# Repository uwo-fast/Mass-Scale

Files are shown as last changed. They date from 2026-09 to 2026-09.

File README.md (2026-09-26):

# Mass Scale

> A 3-D printed digital scale built around a strain-gauge load cell, an HX711
> amplifier and an Arduino Nano, read over serial for data logging. Three
> generations in one repository: Benjamin Hubbard's 2019 OS Nano Balance, the
> lab-grade scale Michigan Tech's MOST lab published in *Instruments* in 2020,
> and the FAST research group's 2025–26 revival, which is the current design.





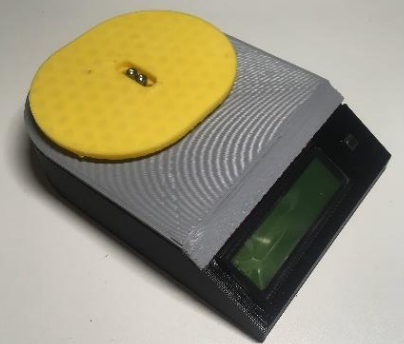
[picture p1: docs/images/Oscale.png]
The assembled 2020 scale: the printed housing with its yellow weighing platform and the LCD


## Overview

The scale is a printed housing that holds a single-point parallel-beam load
cell (a TAL220 for kilogram ranges or a TAL221 for gram ranges), an HX711
24-bit load-cell amplifier, an Arduino Nano, a push-button, and optionally a
16 × 2 LCD. Everything runs from 5 V over USB, so a phone charger or a
computer's USB port powers it. The button tares the scale; over serial, a
computer reads it continuously and calibrates it against a known mass.

**The current design** is the revival's:

- [`cad/openscad/`](cad/README.md#the-current-design) — the OpenSCAD v2
  enclosure, with a bevelled front face for the LCD, and the platter that
  fits over it. Parametric: the dimensions are variables at the top of
  `assembly.scad`. [`cad/openscad-v3/`](cad/README.md) is the next revision,
  in progress, with a sliding, latching lid.
- [`firmware/mass-scale/`](firmware/README.md) — the rewritten firmware:
  calibration over serial, stored in EEPROM; tare from the button or serial;
  a non-blocking readout of raw and calibrated values ten times a second;
  guards against a missing amplifier or a corrupt calibration.

The 2020 design and firmware are kept in full and still checked, and the 2019
files are kept for reference and attribution; see [History](#history) and
[`docs/sources.md`](docs/sources.md).

The scale is described in:

> Hubbard BR, Pearce JM (2020). *Open-Source Digitally Replicable Lab-Grade
> Scales.* Instruments 4(3): 18.
> [doi:10.3390/instruments4030018](https://doi.org/10.3390/instruments4030018)

The paper tests three load cells, a 5 kg TAL220 and 500 g and 100 g TAL221s,
against two commercial laboratory balances and against standard masses. It
reports repeatability within 0.05 g for all three, down to a standard deviation
of about 0.005 g for the 100 g cell, readings that track the laboratory balances
linearly, and a parts cost of about USD 51 without an LCD or USD 66 with one
(USD 41 and 47 counting only the parts used out of bulk packs), against USD 110
to 289 for commercial scales with a serial interface.

**Status.** The v2 enclosure and platter have been printed, and the firmware
builds and has had its calibration and readout reworked since; neither has
been characterised the way the paper characterised the 2020 scale. The v2 parts do not yet model the load cell's
mounting or the electronics' seats, and v3 is unfinished; the firmware does
not yet have the 2020 firmware's SMA protocol, OLED support or averaging
filter. See [Known problems](#known-problems) and the issues.

## Repository layout

- `cad/` — every generation of the printed parts: `openscad/` (current),
  `openscad-v3/` (in progress), `openscad-v1/`, `freecad-2020/` with the
  published STLs, `freecad-2019/`, `openscad-2019/`
  ([details](cad/README.md))
- `firmware/` — `mass-scale/` (current), `most-massbalance-2020/` (the paper's
  sketch and the library form of it), `os-nano-balance-2019/`
  ([details](firmware/README.md))
- `electronics/` — the 2020 Fritzing circuit and its breadboard and schematic
  views ([details](electronics/README.md)); the pins are the same in every
  generation
- `bom/` — the paper's bill of materials ([as tables](bom/README.md))
- `docs/` — the 2020 [operation guide](docs/operation.md), the
  [breadboard assembly guide](docs/electronics-assembly.md),
  [the paper](docs/paper/), the [datasheets](docs/datasheets/README.md), the
  [test data](docs/test-data/README.md), the
  [serial protocol notes](docs/serial-protocol/README.md), and
  [sources](docs/sources.md) for everything else
- `tools/` — the STL and FreeCAD comparison scripts the checks use

## Getting started

You need [OpenSCAD](https://openscad.org/),
[arduino-cli](https://arduino.github.io/arduino-cli/), Python 3, `curl`,
`unzip` and [just](https://github.com/casey/just). FreeCAD 0.18 or later
opens the 2020 and 2019 CAD; it is not needed for the checks.

```sh
just firmware-deps   # install the pinned AVR core and libraries; fetch the pinned HX711 and LiquidCrystal
just check           # check the FreeCAD files and STLs, render every OpenSCAD part, build every firmware target (what CI runs)
just render          # write every OpenSCAD part to build/cad/openscad/
just firmware        # build every firmware target and leave the .hex files under build/firmware/
```

`OPENSCAD` names the OpenSCAD command when it is not on `PATH`, and
`OPENSCAD_FLAGS` adds flags to every render.

To build one: render `enclosure` and `platter` from `cad/openscad/`
(`just render`, or the customizer in OpenSCAD's GUI with `assembly.scad`), buy
the parts in [`bom/`](bom/README.md) (the electronics are the same in every
generation), wire them as in [`firmware/README.md`](firmware/README.md#wiring)
or the [breadboard guide](docs/electronics-assembly.md), and flash the
firmware:

```sh
just firmware
arduino-cli upload --fqbn arduino:avr:nano -p /dev/ttyUSB0 --input-dir build/firmware/mass-scale
```

Then open a serial monitor at 115200 baud (newline line endings). The scale
tares itself at start-up and prints `Raw: …, Mass: … g`; `t` or the button
tares it, and `c`, `u00` with the platter empty, then `a<grams>` with a known
mass on it, calibrates it and stores the result in EEPROM. Any serial client
that logs, such as PuTTY, records the readings.
[`firmware/mass-scale/README.md`](firmware/mass-scale/README.md) has the
details; [`docs/operation.md`](docs/operation.md) describes the 2020 firmware
and its SCP-0499 commands.

## Known problems

Carried over from the published designs, or opened by the revival, and not
fixed here; each is an issue:

- **Drift after power-on.** The paper observes that the reading drifts
  noticeably when the scale is first switched on, largely with temperature,
  and recommends a warm-up; no firmware here compensates for temperature.
- **The current firmware lacks features of the 2020 firmware:** the SMA
  SCP-0499 serial protocol, the OLED display driver, the configurable
  averaging filter, and the library form that other sketches can use.
- **The v2 enclosure has no load-cell mount or electronics seats**, and v3 is
  unfinished; the 2020 FreeCAD design has both.
- **The OLED display is unstable on small boards** (2020 library). Upstream's
  README says an OLED needs more RAM than a Nano has (use a Nano Every or a
  Mega), and that turning an OLED off and straight back on with `XL` can stall
  the firmware.
- **The housing is light.** The paper notes that the printed housing would
  deform under heavy loads, which side-loads the load cell; higher-capacity
  cells want a stiffer housing.
- **The published 2020 `Base.stl` predates the FreeCAD document.** It is
  1.25 % smaller than the base the document builds, with the same outline; the
  other three STLs match the document (see [`cad/README.md`](cad/README.md)).
- **The paper's sketch was Windows-only as published**: its includes used
  backslashes, fixed here in three one-line commits (see
  [`CHANGELOG.md`](CHANGELOG.md)). The 2019 sketch is kept as published and
  is not built.
- **Third-party datasheets** are redistributed without a licence statement;
  see [`LICENSING.md`](LICENSING.md).

## History

The repository carries all three histories, joined without rewriting any of
them. An annotated tag marks each source as it was:

| Generation | What | Tags |
| --- | --- | --- |
| **2019 — OS Nano Balance**, Benjamin Hubbard | The first version: an Arduino Nano, an HX711 and a TAL220 or TAL221 in printed parts drawn first in OpenSCAD and then in FreeCAD, with a sketch that calibrates from a button against a fixed mass. Published at [brhubbar/OS_Nano_Balance](https://github.com/brhubbar/OS_Nano_Balance) and on Appropedia as [3D printed digital balance](https://www.appropedia.org/3D_printed_digital_balance). Here: `firmware/os-nano-balance-2019/`, `cad/freecad-2019/`, `cad/openscad-2019/` | `mtu-nanobalance-2019` |
| **2020 — the MOST lab-grade scale**, Benjamin Hubbard and Joshua Pearce | The scale the paper describes: one parametric FreeCAD document, the DigitalMassBalance 2.0.1 sketch implementing the SMA SCP-0499 serial protocol, and its later library form MOST_MassBalance 3.4.0. Published in [*Instruments*](https://doi.org/10.3390/instruments4030018), on [OSF me9a8](https://osf.io/me9a8), at [gitlab.com/mtu-most/most_massbalance](https://gitlab.com/mtu-most/most_massbalance) and on [Appropedia](https://www.appropedia.org/Open_Source_Digitally_Replicable_Lab-Grade_Scales). Here: `cad/freecad-2020/`, `firmware/most-massbalance-2020/`, `electronics/`, `bom/`, `docs/` | `mtu-instruments-2020` (the firmware as published with the paper), `mtu-final-2021` (upstream's last commit), `mtu-osf-2020` (the OSF files as published), and upstream's own `v3.0.0` to `v3.4.0` |
| **2025–26 — the FAST revival**, Cameron Brooks | A new OpenSCAD enclosure and platter (v2), a next revision in progress (v3) using the [load-cell-scad](https://github.com/CameronBrooks11/load-cell-scad) library, and a rewrite of the 2019 firmware with calibration over serial. Published at [uwo-fast/mass-scale](https://github.com/uwo-fast/mass-scale), which this repository continues. Here: `cad/openscad/`, `cad/openscad-v3/`, `cad/openscad-v1/`, `firmware/mass-scale/` | `fast-revival-2026` |

[`CHANGELOG.md`](CHANGELOG.md) lists what changed when the histories were
joined and when the 2020 files were imported; [`docs/sources.md`](docs/sources.md)
says where every file came from and what was left out.

## Citation

If you use this scale, please cite the paper above. GitHub's **Cite this
repository** button gives it, from [`CITATION.cff`](CITATION.cff), which also
references the 2019 and revival work.

## License

This repository is licensed by component: the current firmware and the 2019
and 2020 firmware and design files are `GPL-3.0-or-later`; the revival's
OpenSCAD designs are `GPL-3.0-or-later` and `CERN-OHL-S-2.0`, at your option;
the bundled libraries are `MIT` and `LGPL-2.1-or-later` and the vendored
load-cell-scad `GPL-3.0`; the paper and the guides adapted from it are
`CC-BY-4.0`, the Appropedia material `CC-BY-SA-4.0`, and the datasheets state
none. [`LICENSING.md`](LICENSING.md) states what applies where, including the
questions still open.

## Contact

Maintained by the [FAST research group](https://uwo-fast.github.io/). For
research collaboration inquiries, contact Dr. Joshua Pearce
(<joshua.pearce@uwo.ca>).

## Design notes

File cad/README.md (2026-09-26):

# CAD

Every generation of the scale's printed parts, one directory each. The
current design is [`openscad/`](openscad/); the rest are kept as published,
for reference, and are still checked.

| Directory | What it is | Tool | Checked by |
| --- | --- | --- | --- |
| [`openscad/`](openscad/) | **The current design (2025–26, OpenSCAD v2):** `enclosure.scad`, a 150 × 100 × 30 mm shell with 15 mm corner radii, 3 mm walls and a 35° front bevel carrying the cutout, backlight recess and four mounting holes of a 16 × 2 LCD; `platter.scad`, the plate that fits over it with a 0.2 mm allowance; `assembly.scad`, which places both and sets the dimensions; `_settings.scad` (`$fn`, z-fighting offset); `lib/trapezium.scad`, a helper from the lab's other designs, not yet used. Printed in October 2025 with the walls thickened for a 0.8 mm nozzle | OpenSCAD | `just check-scad` renders the enclosure, the platter and the assembly |
| [`openscad-v3/`](openscad-v3/) | **In progress (2026-06):** `mass-scale.scad`, the enclosure re-centred on the origin with a sliding lid, guide channels and latch posts, and the LCD bevel; `test_load_cells.scad`, an exercise of the load-cell and amplifier-board models in `lib/load-cell-scad/` (vendored, see [its README](openscad-v3/lib/load-cell-scad/README.md)), which `mass-scale.scad` does not use yet. What is still missing is listed in the repository's issues | OpenSCAD | `just check-scad` renders the enclosure, the lid and the load-cell exercise |
| [`openscad-v1/`](openscad-v1/) | the 2019 OpenSCAD parts reformatted by the revival (2025), without `Cover.scad` and with the snap joints of the base commented out | OpenSCAD | not rendered by `just check` (they render without warnings) |
| [`freecad-2020/`](freecad-2020/) | **The paper's design (2020):** `Mass Balance.FCStd`, one document with four PartDesign bodies, **Base**, **Top**, **Bed** and **Cover**, driven by a `param` spreadsheet, and `stl/`, the four STLs published with it (2020-06-29) | FreeCAD 0.18 | `just check-cad`; `just compare-freecad` re-exports the bodies |
| [`freecad-2019/`](freecad-2019/) | Benjamin Hubbard's three FreeCAD parts (base, bed, face) with their parameter sheet, in both revisions of the base ([which is which](freecad-2019/README.md)) | FreeCAD 0.18 | `just check-cad` |
| [`openscad-2019/`](openscad-2019/) | Hubbard's original OpenSCAD parts (November 2019): `Base.scad`, `Bed.scad`, `Cover.scad`, with `LoadCellRx.scad` (receivers for the TAL220 and TAL221 with M4 or M5 screws), `TAL220.scad`, `TAL221.scad` and `snap_joint.scad`; they accommodate a TAL220 or TAL221 but no LCD | OpenSCAD | not rendered by `just check` (they render without warnings) |

`parts.tsv` lists every FreeCAD body with its published STL, and
`scad-parts.tsv` every OpenSCAD part that `just check-scad` renders and
`just render` writes to `build/cad/openscad/`. `OPENSCAD` names the OpenSCAD
command when it is not on `PATH`; `OPENSCAD_FLAGS` adds flags to every render.

## The current design

`assembly.scad` is the file to open. Its `test_*` variables set the body
(150 × 100 × 30 mm, 15 mm corner radius, 3 mm walls and top, 35° bevel) and
the platter (4 mm high, 3 mm walls, 0.2 mm allowance around the body), and
`show_platter`, `show_enclosure` and the two `*_cross_section` flags choose
what is drawn. The LCD's dimensions and hole spacing are at the top of
`enclosure.scad` (24.5 × 71.5 mm window, holes 30 × 74.5 mm apart, 3.1 mm),
with a note to turn them into a lookup table for other displays. Neither file
models the load cell's mounting or the electronics' seats, which the 2020
design has; see the repository's issues.

Render from the command line, from `cad/openscad/`:

```sh
openscad -D show_platter=false   -o enclosure.stl assembly.scad
openscad -D show_enclosure=false -o platter.stl   assembly.scad
```

or `just render` for every listed part.

## The 2020 design

The `param` spreadsheet in `freecad-2020/Mass Balance.FCStd` sets the body at
110 × 155 × 30 mm with a 2 mm shell and a 45 mm corner radius, the 40 × 60 mm
solder breadboard's seat, the 72 × 27 mm screen cutout, the 6 mm push-button
opening, the Nano's USB slot, and the boss height and screw spacing for each of
the two load cells (TAL220: 15 mm spacing, 62.5 mm from the bed centre; TAL221:
6 mm spacing, 40 mm from the centre). Change a value there and the four bodies
follow. Every part locates by features of the prints themselves, bosses and
snap joints, so the only fasteners are the ones that hold the load cell.

By their dimensions, the published STLs are:

| STL | Bounding box (mm) | Part |
| --- | --- | --- |
| `Base.stl` | 110 × 155 × 30 | the base: houses the circuit board and the LCD, and carries the two load-cell bosses |
| `Top.stl` | 110 × 125 × 7 | the lid that snaps onto the base and encloses the electronics ("cover" in the paper's Table 1) |
| `Bed.stl` | 100 × 80 × 14 | the weighing bed, bolted to the free end of the load cell |
| `Cover.stl` | 107 × 87 × 22 | the optional cover that sits over the bed to shield it from air currents, printed in translucent PETG in the paper |

`just check` confirms each document is an intact FreeCAD archive holding the body
[`parts.tsv`](parts.tsv) names, and that each STL encloses a positive volume
(`just stl-stats` prints them). The STLs are the author's exports; CI does not
re-export them, because it has no FreeCAD.

### How the published STLs compare with the source

`just compare-freecad` runs [`../tools/export_freecad.py`](../tools/export_freecad.py)
under `freecadcmd`, FreeCAD's headless interpreter: it opens
`Mass Balance.FCStd`, recomputes it, reports any object that does not reach the
up-to-date state, writes each body to `build/cad/freecad/` as binary STL with
`MeshPart.meshFromShape` at a 0.01 mm linear deflection, and compares each
export with the published file by volume and bounding box
(`tools/stlcmp.py`). It needs FreeCAD on the machine (`FREECADCMD` names the
interpreter when it is not on `PATH`); tessellations differ between exports,
so a re-export is compared by volume and bounding box, not by hash.

With FreeCAD 1.1.3, the document (saved by 0.18R4) opens with one deprecation
notice, that the feature on `Sketch001` sets the old `Midplane` property in
place of `SideType`, and a full recompute leaves every object up to date. The
recomputed bodies have the same volume as the shapes saved in the file, to four
decimals of a percent, so what follows compares the saved design with the
published STLs:

| Body | Published STL | Export | Published | Difference |
| --- | --- | --- | --- | --- |
| Base | `Base.stl` | 63300.7 mm³, 110 × 155 × 30 mm | 62517.0 mm³, 110 × 155 × 30 mm | +1.25 % |
| Top | `Top.stl` | 28050.8 mm³, 110 × 125.02 × 7 mm | 28048.5 mm³, 110 × 125.02 × 7 mm | +0.01 % |
| Bed | `Bed.stl` | 28167.5 mm³, 100 × 80 × 14 mm | 28166.1 mm³, 99.98 × 80 × 14 mm | +0.01 % |
| Cover | `Cover.stl` | 14129.6 mm³, 107 × 87 × 22 mm | 14128.0 mm³, 107 × 87 × 22 mm | +0.01 % |

Top, Bed and Cover match to within tessellation. The published `Base.stl` is
784 mm³ smaller than the document's Base body: it carries a 2020-02-18
timestamp in the OSF archive, two days before the document's last save
(2020-02-20, by its own metadata), and the Base body's last four features (the
screen holder, two PCB retainers and the cable-management pad) add 915 mm³
after the USB slot, where the body is 62388 mm³. No single feature boundary
reproduces 62517 mm³, so the published file is an export of an intermediate
state of the base, and the document holds the later design. The bounding boxes
are identical, so the difference is inside the shell.

The paper prints the parts in PLA on a LulzBot TAZ 6 at 0.14 mm layers with 20 %
cubic infill (Table 2 of the paper), and notes that all of them can be printed
without support depending on the finish wanted.

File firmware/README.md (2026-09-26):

# Firmware

Three generations of the scale's firmware, all for an Arduino Nano (ATmega328P)
reading an HX711 load-cell amplifier, with an optional 16 × 2 LCD. The current
one is [`mass-scale/`](mass-scale/); the other two are kept as published.

| Directory | What it is | By | Built by `just check` |
| --- | --- | --- | --- |
| [`mass-scale/`](mass-scale/) | **The current firmware (2025–26):** a rewrite of the 2019 sketch with calibration driven over serial (`c`, `u00`, `a<grams>`), the sensitivity stored in EEPROM, tare from the button or `t`, a debounced button, a non-blocking 100 ms readout of the raw and calibrated values, and guards against a missing HX711 or a corrupt calibration ([details](mass-scale/README.md)) | Cameron K. Brooks, derived from the 2019 sketch | yes, against bogde/HX711 0.7.5 and LiquidCrystal 1.0.7 fetched by `just firmware-libs` |
| [`most-massbalance-2020/`](most-massbalance-2020/) | **The paper's firmware (2020):** `DigitalMassBalance`, the 2.0.1 sketch the paper describes, and `MOST_MassBalance`, its later library form (3.4.0) with LCD and OLED display drivers and an averaging filter. Both implement the Scale Manufacturers Association's SCP-0499 serial protocol to Level 2 ([details](most-massbalance-2020/README.md)) | Benjamin Hubbard | yes, both |
| [`os-nano-balance-2019/`](os-nano-balance-2019/) | **The 2019 sketch:** `OS_Nano_Balance.ino`, with a calibrate button (D7) as well as tare (D8), a fixed 235.9 g calibration mass and readings in kilograms; kept with the project's [README](os-nano-balance-2019/README.md) of the time | Benjamin Hubbard | no: it includes the HX711 and LiquidCrystal libraries at the paths of its own repository's git submodules (`src\HX711\src\HX711.h`), which are not here |

## Wiring

All three use the same pins, so a scale wired for one runs any of them.

| Function | Pin | Notes |
| --- | --- | --- |
| HX711 DT | D2 | |
| HX711 SCK | D3 | |
| HX711 VCC | D4 | the HX711 (1.5 mA) is powered from a digital pin, so it can be switched off |
| LCD power | D5 | as above (the LCD draws about 2.5 mA) |
| Tare button | D8 | to ground; internal pull-up |
| Calibrate button | D7 | 2019 sketch only; the 2020 sketch defines it but does not use it |
| LCD RS, E, D4–D7 | A0, A1, A2–A5 | 4-bit mode, as Arduino's LiquidCrystal "Hello World" |

Load cell to HX711: red to E+, black to E-, green to A+, white to A-. The
2020 design's Fritzing circuit and breadboard photographs are in
[`../electronics/`](../electronics/README.md) and
[`../docs/electronics-assembly.md`](../docs/electronics-assembly.md).

## Building and flashing the current firmware

```sh
just firmware-deps   # once: the pinned AVR core and libraries
just firmware        # build/firmware/mass-scale/mass-scale.ino.hex, and the 2020 targets
arduino-cli upload --fqbn arduino:avr:nano -p /dev/ttyUSB0 --input-dir build/firmware/mass-scale
```

Or compile and upload the sketch directly, naming the fetched libraries so
they take priority over any of the same name installed for the user:

```sh
arduino-cli compile --fqbn arduino:avr:nano \
  --library build/deps/libraries/HX711 --library build/deps/libraries/LiquidCrystal \
  firmware/mass-scale
arduino-cli upload --fqbn arduino:avr:nano -p /dev/ttyUSB0 firmware/mass-scale
```

Clones with the older bootloader need `--fqbn arduino:avr:nano:cpu=atmega328old`.
In the Arduino IDE, install "HX711 Arduino Library" (Bogdan Necula) and
"LiquidCrystal" from the Library Manager and open `mass-scale/mass-scale.ino`.

Then open a serial monitor at 115200 baud with newline line endings: the scale
tares itself at start-up, prints `Raw: …, Mass: … g` ten times a second, tares
on `t` or the button, and calibrates on `c` followed by `u00` with the platter
empty and `a<grams>` with a known mass on it (`x` aborts). The result is
stored in EEPROM. Any serial client that logs, such as PuTTY, records the
readings; Arduino's Serial Plotter shows them live.

## What the current firmware does not do yet

Compared with the 2020 firmware it replaces: it does not speak the SMA
SCP-0499 protocol (it has its own single-letter commands), has no OLED
driver, no configurable averaging filter and no logging beyond what a serial
client captures. These are tracked as issues.

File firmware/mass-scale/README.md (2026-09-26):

# mass-scale

Arduino firmware for a 3D-printable digital mass balance using an HX711 load-cell amplifier and optional 16×2 LCD.

The firmware provides:

- Live raw and calibrated mass readings
- Serial and push-button tare
- Serial-guided calibration
- EEPROM calibration storage
- Automatic zeroing at startup

## Hardware

- Arduino-compatible board
- HX711 load-cell amplifier
- Load cell
- Optional HD44780-compatible 16×2 LCD
- Optional momentary tare button

## Pin Configuration

| Function    |   Pin |
| ----------- | ----: |
| HX711 DT    |     2 |
| HX711 SCK   |     3 |
| HX711 power |     4 |
| LCD power   |     5 |
| Tare button |     8 |
| LCD RS      |    A0 |
| LCD Enable  |    A1 |
| LCD D4–D7   | A2–A5 |

The tare button connects pin 8 to ground and uses the internal pull-up resistor.

## Dependencies

- `HX711` — the "HX711 Arduino Library" by Bogdan Necula
  ([bogde/HX711](https://github.com/bogde/HX711)), 0.7.5
- `LiquidCrystal` ([arduino-libraries/LiquidCrystal](https://github.com/arduino-libraries/LiquidCrystal)), 1.0.7

`EEPROM` is provided by the Arduino core. From the repository, `just firmware-libs`
fetches both libraries at those versions into `build/deps/libraries/` and
`just check-firmware` and `just firmware` build against them; in the Arduino
IDE, install them from the Library Manager.

## Configuration

Set the fallback calibration factor in `defaults.h`:

```cpp
#define default_scale 0.016016
```

Set `isLCD` to `false` when no LCD is connected.

## Usage

Flash the firmware, then open the serial monitor at:

- **115200 baud**
- **Newline** line ending

The scale automatically tares during startup. The attached platter must therefore be installed and unloaded when the device powers on.

### Serial Commands

| Command | Action            |
| ------- | ----------------- |
| `t`     | Tare the scale    |
| `c`     | Start calibration |

The tare button performs the same operation as the `t` command.

### Calibration

1. Remove all removable weight while leaving the permanent platter installed.
2. Send `c`.
3. Send `u00` when the scale is unloaded.
4. Place a known mass on the scale.
5. Send `a` followed by the mass in grams (or `x` to abort).

For a 500 g calibration mass:

```text
c
u00
a500
```

The calculated sensitivity is stored in EEPROM and restored automatically after restart.

For best results, use a calibration mass near the normal operating range and wait for the load-cell reading to stabilize before entering its value.

## Output

The serial monitor reports the tare-subtracted raw HX711 reading and calibrated mass:

```text
Raw: 617283.00, Mass: 500.00 g
```

The LCD, when enabled, displays the mass in grams.

## License

Copyright © 2025 Cameron K. Brooks.

This project is licensed under the GNU General Public License, version 3 or later.

It is derived from `OS_Nano_Balance`, Copyright © 2019 Benjamin Hubbard.

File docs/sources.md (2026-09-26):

# Sources

Where everything in this repository came from, and what else exists about the
scale that is not copied here. Collected in September 2026.

## The three generations

| Generation | Where | In this repository |
| --- | --- | --- |
| **2019, OS Nano Balance**, Benjamin Hubbard | [github.com/brhubbar/OS_Nano_Balance](https://github.com/brhubbar/OS_Nano_Balance) (`GPL-3.0`), documented on Appropedia as [3D printed digital balance](https://www.appropedia.org/3D_printed_digital_balance) | full history, tag `mtu-nanobalance-2019`; the sketch in [`../firmware/os-nano-balance-2019/`](../firmware/os-nano-balance-2019/), the FreeCAD parts in [`../cad/freecad-2019/`](../cad/freecad-2019/), the OpenSCAD parts in [`../cad/openscad-2019/`](../cad/openscad-2019/) |
| **2020, the MOST lab-grade scale**, Benjamin Hubbard and Joshua Pearce | the paper, OSF, GitLab and Appropedia listed under [Primary](#primary) below | full history of the firmware library, tags `mtu-instruments-2020`, `mtu-final-2021` and `mtu-osf-2020`; the design in [`../cad/freecad-2020/`](../cad/freecad-2020/), the firmware in [`../firmware/most-massbalance-2020/`](../firmware/most-massbalance-2020/) |
| **2025–26, the revival**, Cameron Brooks, FAST research group | [github.com/uwo-fast/mass-scale](https://github.com/uwo-fast/mass-scale), the repository this one continues | full history, tag `fast-revival-2026`; the designs in [`../cad/openscad/`](../cad/openscad/), [`../cad/openscad-v3/`](../cad/openscad-v3/) and [`../cad/openscad-v1/`](../cad/openscad-v1/), the firmware in [`../firmware/mass-scale/`](../firmware/mass-scale/) |

## Primary

| What | Where |
| --- | --- |
| Paper, 2020 | [doi:10.3390/instruments4030018](https://doi.org/10.3390/instruments4030018), open access, `CC-BY-4.0` · in [`paper/`](paper/) · a [preprint](https://www.preprints.org/manuscript/202004.0472/v1) and an [author copy](https://digitalcommons.mtu.edu/michigantech-p/2052) also exist |
| Firmware library, with history | [gitlab.com/mtu-most/most_massbalance](https://gitlab.com/mtu-most/most_massbalance), included here (tags `mtu-instruments-2020`, `mtu-final-2021`, and upstream's own `v3.0.0` to `v3.4.0`) |
| CAD, the paper's sketch, circuit, datasheets and test data | [OSF me9a8](https://osf.io/me9a8), "Open source laboratory logging digital scale" (DOI 10.17605/OSF.IO/ME9A8), imported unchanged in the commit tagged `mtu-osf-2020` |
| Project page, with the breadboard assembly guide | [Appropedia: Open Source Digitally Replicable Lab-Grade Scales](https://www.appropedia.org/Open_Source_Digitally_Replicable_Lab-Grade_Scales), adapted in [`electronics-assembly.md`](electronics-assembly.md) |
| STLs, mirrored | [MyMiniFactory 126135](https://www.myminifactory.com/object/3d-print-open-source-digitally-replicable-lab-grade-scale-126135), linked from Appropedia as the "quick download" (not fetched: the site sits behind a browser check) |
| Use video | "MOST OS Balance.mpeg" on OSF, the paper's Video S1; attached to this repository's first release (see below) |
| The 2019 project's page | [Appropedia: 3D printed digital balance](https://www.appropedia.org/3D_printed_digital_balance) (its older title, "3-D Printable Digital Balance", redirects there) |

Libraries the firmware uses, with their upstreams: the
[HX711 library](https://github.com/bogde/HX711) by Bogdan Necula (`MIT`),
bundled with the 2020 firmware at 0.7.4 and fetched at 0.7.5 for the current
firmware by `just firmware-libs`; Arduino's
[LiquidCrystal](https://github.com/arduino-libraries/LiquidCrystal)
(`LGPL-2.1-or-later`), bundled with the 2020 sketch at 1.0.7 and fetched at
the same version for the current firmware. The 2020 library's OLED support
uses Adafruit's [SSD1306](https://github.com/adafruit/Adafruit_SSD1306),
[GFX](https://github.com/adafruit/Adafruit-GFX-Library) and
[BusIO](https://github.com/adafruit/Adafruit_BusIO) libraries, installed by
`just firmware-deps` rather than bundled.

The v3 design's load-cell and amplifier models come from
[CameronBrooks11/load-cell-scad](https://github.com/CameronBrooks11/load-cell-scad)
(`GPL-3.0`), copied at commit `c8f224a` (2026-07-01) into
[`../cad/openscad-v3/lib/load-cell-scad/`](../cad/openscad-v3/lib/load-cell-scad/README.md).

The 2020 firmware's serial interface implements the Scale Manufacturers
Association's SCP-0499 protocol; the standard and the association's load-cell
test guideline are linked from [`datasheets/`](datasheets/README.md).

## Related

- **The 2020 sketch's README** is the 2019 project's README with a few items
  struck through, and the revival's README was the same document updated for
  the serial-driven firmware; the 2019 original is kept at
  [`../firmware/os-nano-balance-2019/README.md`](../firmware/os-nano-balance-2019/README.md).
- **The upstream repository's earlier home.** The library's history starts on
  GitHub in January 2020 (its merge commits name pull requests there) and moved
  to the MOST group's GitLab in 2020; the GitHub copy no longer exists.

## Not included

- **The use video**, `Documentation/MOST OS Balance.mpeg` on OSF: 370,255,096
  bytes, MPEG-2 program stream, MD5 `66f02c4be425f369919c497e4ba0343c`. Too
  large for the repository; attached to its first release instead.
- **The Denver Instruments manuals** for the A-160 analytical balance and the
  APX402 balance the paper compared against (`Denver A-160 Operators
  Manual.pdf`, MD5 `16764d6581afa8f9837330ee14bca2db`; `Denver APX402
  Operators Manual.pdf`, MD5 `1d14f42e87e6531837753cf2fd0bd2c6`): third-party
  documents about instruments that are not part of the design. The paper cites
  them at denverinstrument.com (references 90 and 91). Reachable through the
  `mtu-osf-2020` tag.
- **The SMA protocol tester**, `SCPTesterProgram.zip` (a 2004 Windows
  installer, MD5 `8c11f268e9889f2dac8af41f9a3bb681`) and
  `SCPTesterDocumentation.pdf` (MD5 `549957656531bd4c33909fb9253603c0`): the
  Scale Manufacturers Association's own test program, used to check the
  firmware's compliance. Reachable through the `mtu-osf-2020` tag.
- **The SMA standard and test guideline**, `ScaleCommProtocol5199M1.pdf` and
  `loadcellapplicationtestguidelineapril2010.pdf`: the association's
  publications, linked from [`datasheets/`](datasheets/README.md) instead.
  Reachable through the `mtu-osf-2020` tag.
- **Duplicates.** The OSF copies of the Fritzing circuit and the two protocol
  notes, byte for byte the upstream repository's (after line-ending
  normalisation for the notes), and the STL zip, whose four files are stored
  unpacked. The revival's copies of the 2019 FreeCAD parts and of the 2020
  document, and the 2019 and revival copies of the datasheets, byte for byte
  the files kept. Reachable through the `mtu-osf-2020`, `mtu-nanobalance-2019`
  and `fast-revival-2026` tags.
- **Git metadata** of the imports: the 2019 sketch's HX711 submodule (the
  library is a build dependency instead), the sketch's stale `.gitmodules`
  and `.gitignore` on OSF, and the 2019 and revival `LICENSE`, `.gitignore`
  and `.gitattributes` files, which the repository-level files replace.

## Upstream problems found while importing

Fixed, so that the firmware builds on every platform (see
[`../CHANGELOG.md`](../CHANGELOG.md)):

- Both 2020 sketches included their headers with backslashes, and the 2020
  sketch included its bundled libraries at submodule paths that the OSF upload
  does not have.

Documented but not fixed: see the repository's issues and the README's known
problems. The 2019 sketch is kept as published; it includes its libraries at
the submodule paths of its own repository, with backslashes, and is not built
here.

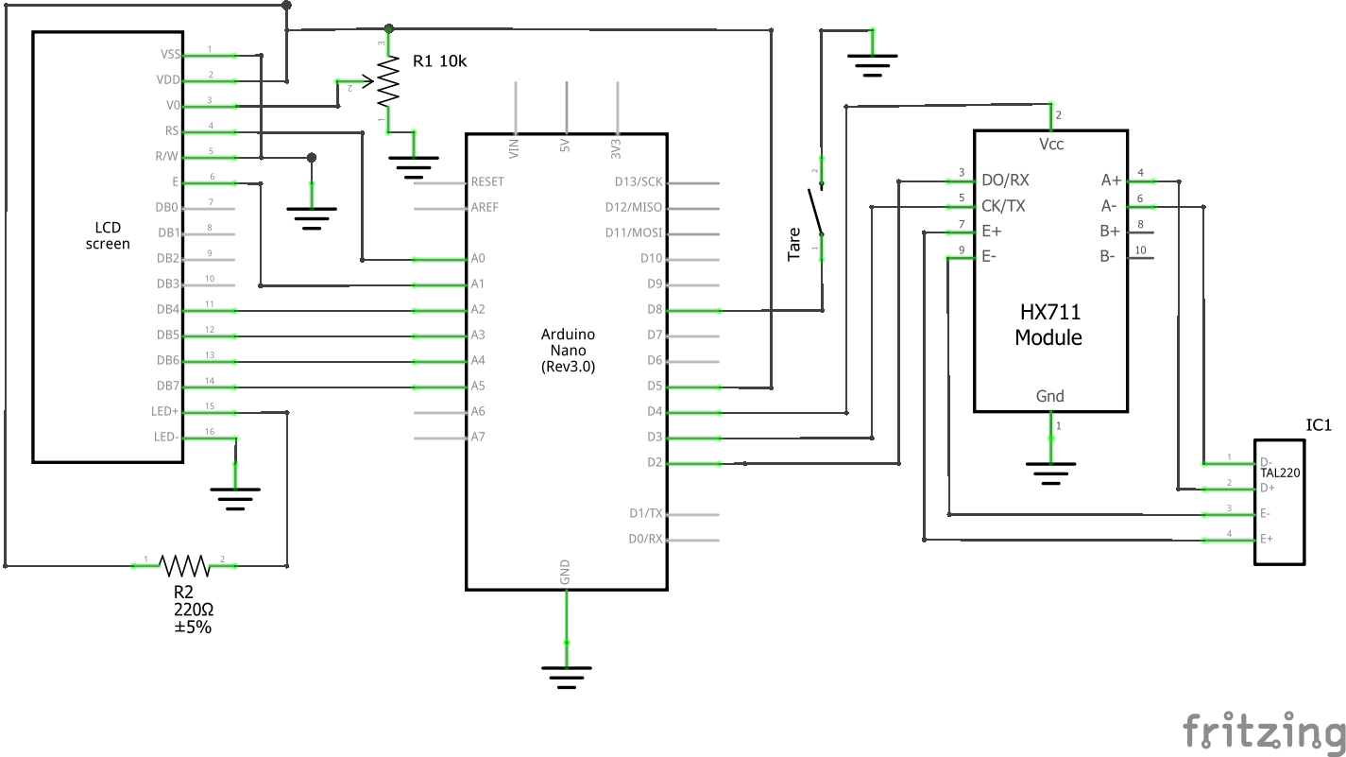
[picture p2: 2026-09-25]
electronics/Circuit Diagram_schem.png

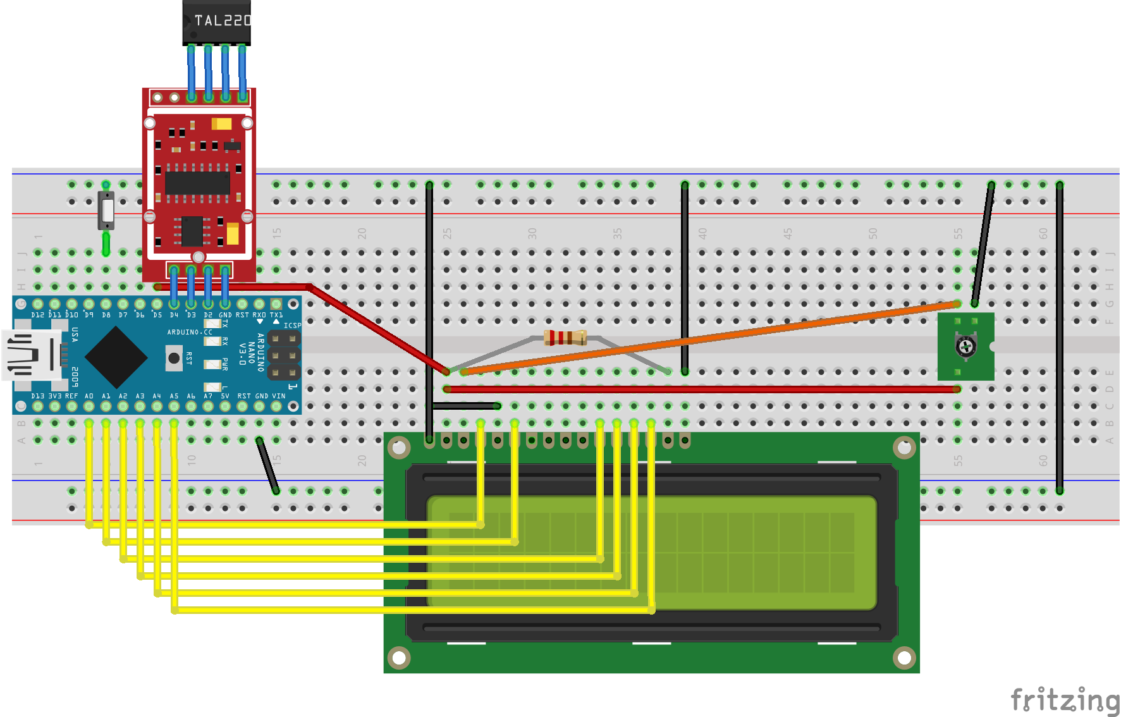
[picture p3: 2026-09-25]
electronics/Circuit Diagram_bb.png

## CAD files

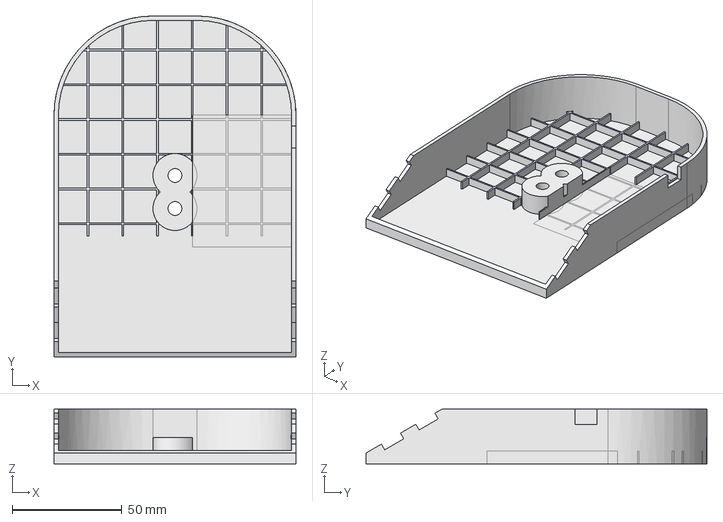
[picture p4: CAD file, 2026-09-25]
cad/freecad-2019/Base-osf.FCStd
110.0 x 155.0 x 25.0 mm

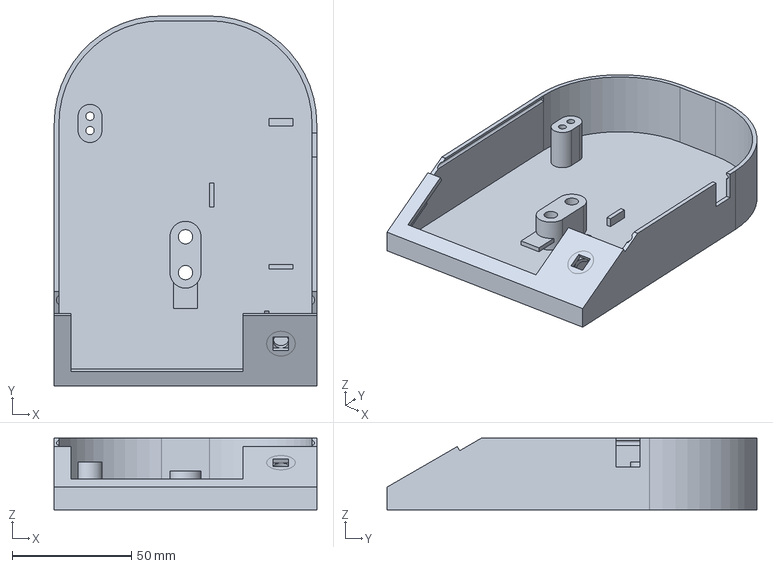
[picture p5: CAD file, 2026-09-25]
cad/freecad-2020/Mass Balance.FCStd
110.0 x 155.0 x 30.0 mm

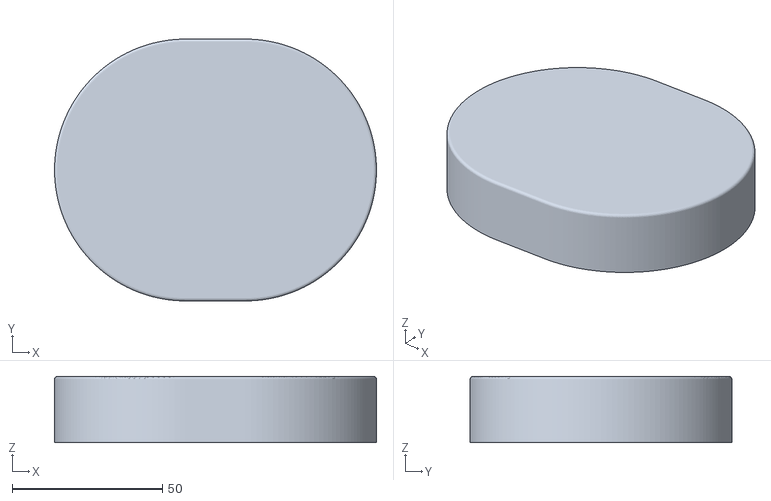
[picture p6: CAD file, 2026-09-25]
cad/freecad-2020/stl/Cover.stl
107.0 x 87.0 x 22.0

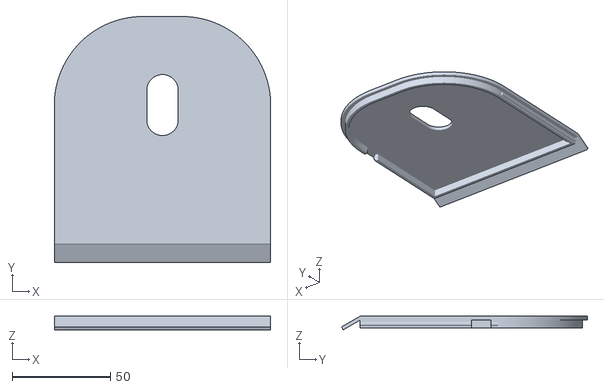
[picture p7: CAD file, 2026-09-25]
cad/freecad-2020/stl/Top.stl
110.0 x 125.0 x 7.00

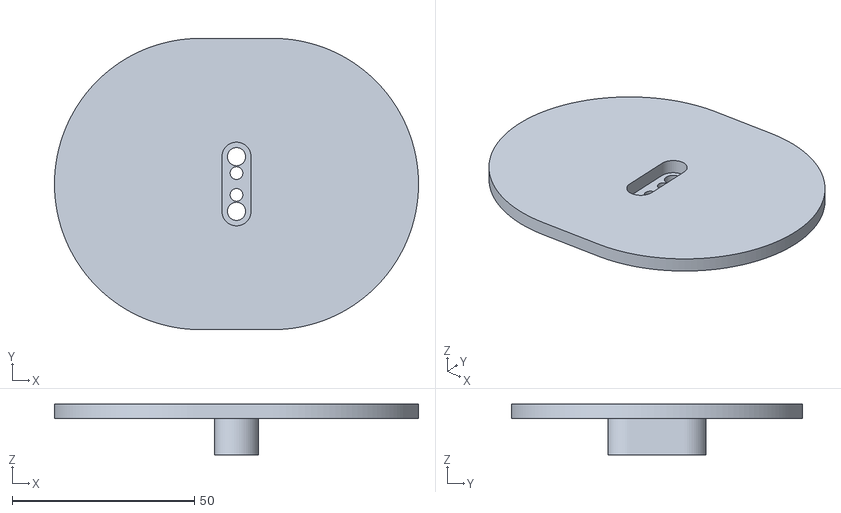
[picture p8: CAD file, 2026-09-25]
cad/freecad-2020/stl/Bed.stl
100.0 x 80.0 x 14.0

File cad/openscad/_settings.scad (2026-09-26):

$fn = $preview ? 32 : 128;
z_fight = $preview ? 0.1 : 0;

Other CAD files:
cad/freecad-2020/stl/Base.stl
cad/openscad-v1/Base.scad
cad/openscad-v1/Bed.scad
cad/openscad-v1/LoadCellRx.scad
cad/openscad-v1/TAL220.scad
cad/openscad-v1/TAL221.scad
cad/openscad-v1/snap_joint.scad
cad/openscad-v3/mass-scale.scad
cad/openscad-v3/test_load_cells.scad
cad/openscad/assembly.scad
cad/openscad/enclosure.scad
cad/openscad/platter.scad

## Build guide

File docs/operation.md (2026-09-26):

# Operating the scale

Adapted from Sections 2.4 and 2.5 of the paper in [`paper/`](paper/):
Hubbard BR, Pearce JM (2020). *Open-Source Digitally Replicable Lab-Grade
Scales.* Instruments 4(3): 18 (`CC-BY-4.0`), and from the protocol notes in
[`serial-protocol/`](serial-protocol/). It describes the
[DigitalMassBalance 2.0.1](../firmware/most-massbalance-2020/DigitalMassBalance/) firmware the paper
was written for; the later [MOST_MassBalance](../firmware/most-massbalance-2020/MOST_MassBalance/)
library keeps the same commands. Text marked **Note** is added here.

The assembled scale

The scale works in two ways: as a simple scale with an LCD and a push-button,
and as a lab scale with a serial interface for data logging and control. A
single firmware does both; `Config.hpp` tells it whether an LCD is fitted, and
the serial interface always listens.

## Start-up

On power, over USB from a computer or a 5 V power block, the firmware:

1. opens a 9600 baud serial connection (it waits for serial to initialise, which
   does not noticeably delay start-up on a plain power supply);
2. powers up the HX711 and checks it is talking, reporting progress over serial;
3. powers up the LCD if one is configured, flashing every digit as `8` for a
   moment;
4. reads the saved calibration sensitivity from EEPROM, if a calibration has
   ever been run, and reports it; otherwise the sensitivity is 1 and the
   readout is the raw HX711 count;
5. clears the averaging filter (10 readings by default, set in `Config.hpp`),
   which sets the scale's response time;
6. sets the tare button as an input with the internal pull-up, so it is active
   low.

After that the scale reads the load cell as fast as it can, keeps a sliding
average, updates the LCD, watches the button, and listens for serial commands,
the last three at the report rate set in `Config.hpp` (1 Hz).

## As a simple scale

- **Tare.** Press and release the button on the front. A dot in the lower right
  corner of the LCD acknowledges the press.
- **Calibrate.** Hold the button for at least 3 s (`CAL_WAIT` in
  `Config.hpp`). The scale tares, then shows the mass to put on the bed (the
  calibration mass in `Config.hpp`, 235.9 g by default, one US cup of water).
  When it detects the added mass it averages 10 readings, works out the new
  sensitivity and saves it to EEPROM.

## As a lab scale over serial

The serial interface follows the Scale Manufacturers Association's SCP-0499
protocol to Level 2: the six Level 1 commands plus extensions. Open the port at
9600 baud. Every command is a character between a line feed and a carriage
return, `<LF>c<CR>`; the `<ESC>` reset is the one exception. The responses,
`<LF><s><r><n><m><f><xxxxxx.xxx><uuu><CR>`, are described in
[`serial-protocol/Response Formats.txt`](serial-protocol/Response%20Formats.txt).

| Command | Does |
| --- | --- |
| `W` | return the displayed weight |
| `Z` | zero the scale (with nothing on the bed) |
| `T` | tare: subtract the mass now on the bed, for instance a container |
| `T<xxxxxx.xxx>` | set the tare weight to the value given |
| `M` | return the stored tare weight |
| `C` | clear the tare, so readings refer to the zero set by `Z` |
| `D` | run the scale diagnostics |
| `A`, `B` | the "about" lines: protocol level, then firmware information |
| `R` | repeat the weight continuously at the report rate, until another command arrives |
| `<ESC>` | software reset; wait a few seconds, then send `A` to confirm the scale is back |
| `XC` | calibrate with the default calibration mass |
| `XC<xxxxxx.xxx>` | calibrate with the mass given; the scale zeroes, echoes the expected mass, measures for two minutes, then reports the new reading |
| `XL` | toggle power to the LCD, for power saving when the display is not needed |
| `XP` | scroll the readout precision between 0 and 4 decimal places |
| `X?` | list the commands (the leading `X` of the extended commands is also announced at the end of start-up) |

**Note:** the commands are single characters after the `<LF>`, so a terminal
program has to send the line feed first; PuTTY with its session logging is what
the paper used to capture data (see [`test-data/`](test-data/README.md)).

## Calibrating for measurements

For the paper's tests the scale was calibrated against a known mass measured on
a laboratory balance, or against a standard mass: the 100 g TAL221 with a 20 g
mass, the 500 g TAL221 and 5 kg TAL220 with 100 g. The electronics were left on
for at least an hour before calibrating and measuring; the paper observes that
the reading drifts noticeably after power-on, largely with temperature, and
that the comparison balances' manuals recommend 15 to 60 minutes of warm-up. A
cover over the bed (`Cover.stl`) reduces the effect of air currents.

## Mounting the load cell

The load cell must be mounted with its wires running toward the end fixed to
the base; wires leaving the floating end interfere with the measurement.

- **TAL220:** bolt the M5 end (the wires run to it) to the TAL220 boss in the
  base, connect the cell to the HX711 (red E+, black E−, white A−, green A+),
  snap the lid onto the base, then bolt the bed to the free end with the two
  M4 screws.
- **TAL221:** the lid is sandwiched between the bed and the load cell. Screw
  the untapped end of the cell (the wires do not run to it) to the bed with M3
  screws and nuts, connect the cell to the HX711 as above, then screw the
  tapped M3 end to the TAL221 boss in the base, by feel, with the lid snapped
  on.

Section 2.3 of the paper has photographs of each step.

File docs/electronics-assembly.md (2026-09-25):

# Assembling the electronics on a solder breadboard

Adapted from the "Electronics Assembly" section of the Appropedia page
[Open Source Digitally Replicable Lab-Grade Scales](https://www.appropedia.org/Open_Source_Digitally_Replicable_Lab-Grade_Scales),
written by Benjamin Hubbard in February 2021 (`CC-BY-SA-4.0`). Text marked
**Note** is added here.

This is one way to wire the scale on a 4 × 6 cm solder breadboard, the way the
third scale was assembled. It follows the schematic in
[`../electronics/`](../electronics/README.md). The breadboard is a grid whose
pads are named by a letter on one axis and a number on the other, as in the
game of Battleship; the pad names below locate every part.

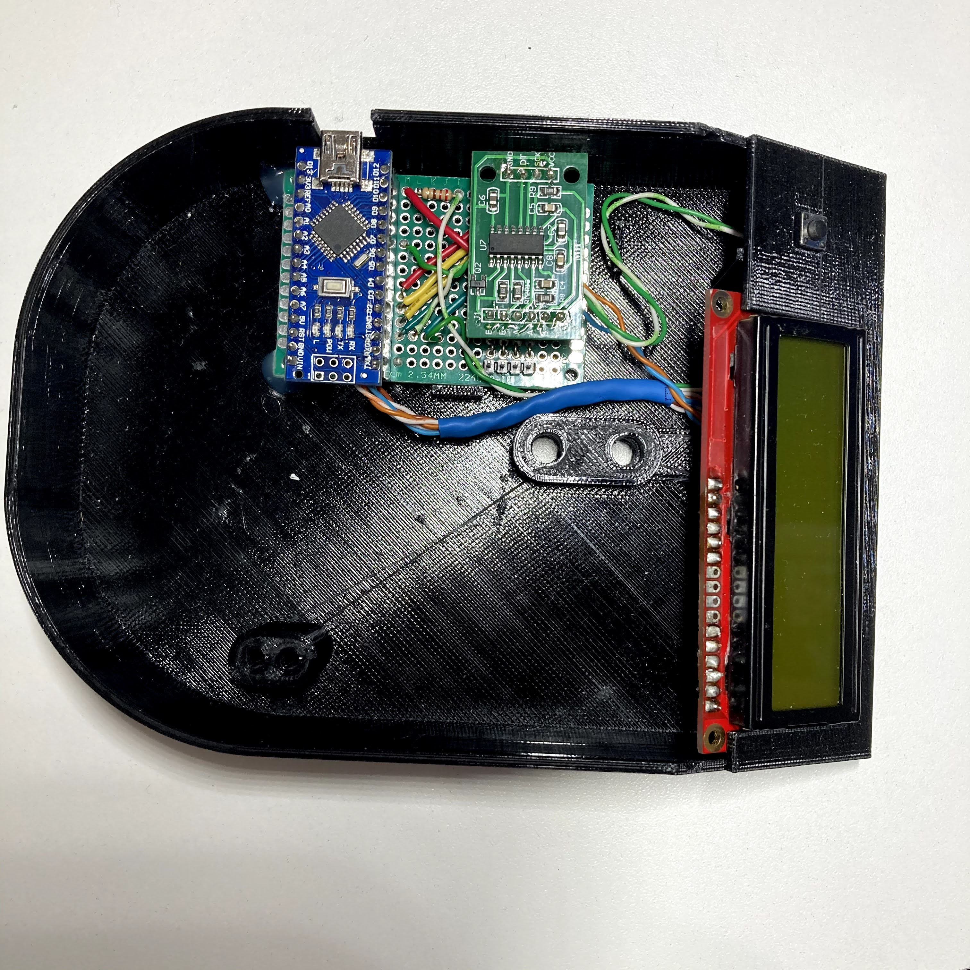
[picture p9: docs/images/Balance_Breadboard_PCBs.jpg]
The finished breadboard with the Arduino Nano and HX711 installed


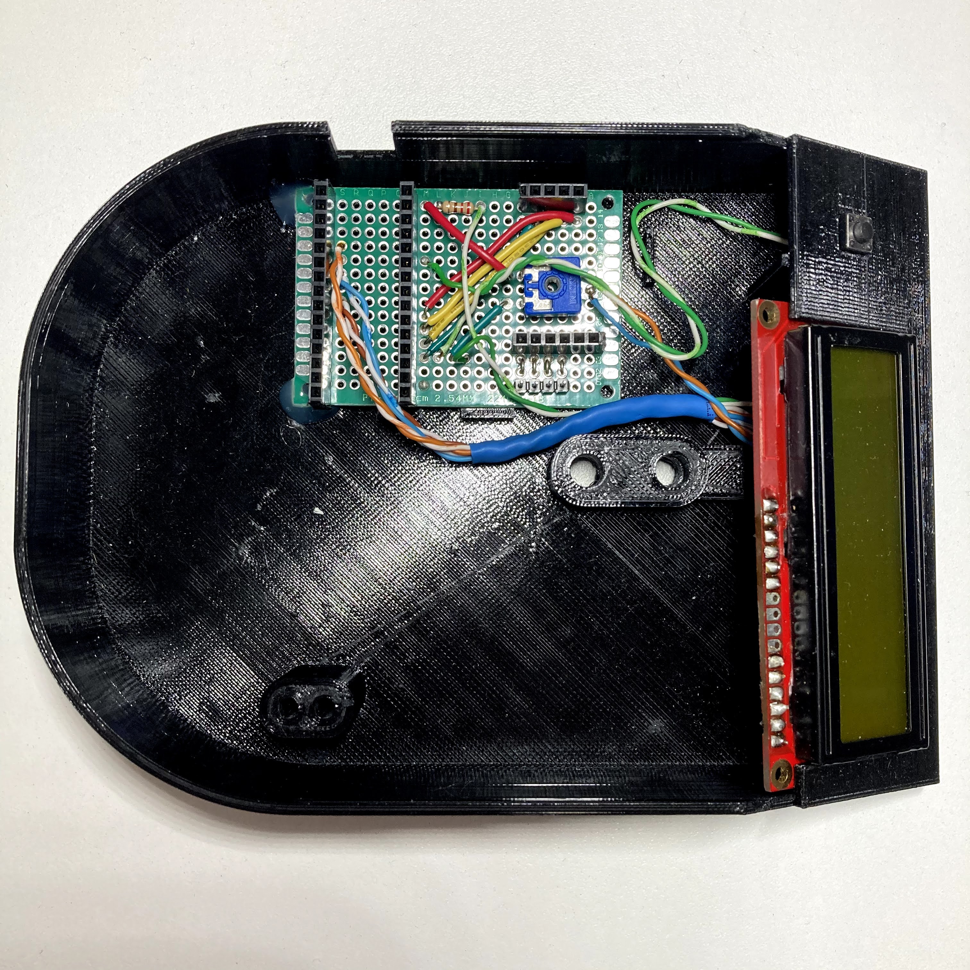
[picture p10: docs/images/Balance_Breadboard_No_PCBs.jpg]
The breadboard before the Nano and HX711 are plugged in, with all wires and pins visible


## Required items

- 4 × 6 cm solder breadboard
- 200 mm (8″) lengths of twisted pair, as from Cat 5 cable:
  - 2 × green / green-white
  - 1 × blue / blue-white
  - 1 × orange / orange-white
  - 1 × brown / brown-white
  - 1 × blue / orange
- 22 AWG solid-core wire:
  - 2 × 40 mm (1.5″) yellow
  - 1 × 20 mm (1″) green
  - 3 × 30 mm (1.25″) green
  - 1 × 40 mm (1.5″) green
  - 1 × 25 mm (1″) red
  - 1 × 45 mm (1.75″) red
  - 4 × 8 mm (0.25″) bare
- 220 Ω resistor
- 10 kΩ trimmer potentiometer
- Female header pins: 2 × 15-pin, 1 × 6-pin, 1 × 4-pin
- Male header pins: 1 × 4-pin
- 16 × 2 LCD
- Normally-open push-button
- Heat shrink: 1 × 45 mm (cut in half), 3 × 45 mm, 5 × 45 mm

**Note:** the header counts here differ from the paper's Table 1, which lists
the parts of an earlier build; see [`../bom/`](../bom/README.md).

## Install the header pins

Solder the headers onto the breadboard as listed.

| Female header | Breadboard position |
| --- | --- |
| 15 × 1 | T0–T14 |
| 15 × 1 | N0–N14 |
| 6 × 1 | A4–F4 |
| 4 × 1 | B14–E14 |

| Male header | Breadboard position |
| --- | --- |
| 4 × 1 | C1–F1 |

Finally, use the four bare pieces of wire to connect the four male header pins
to their four neighbours on the 6 × 1 female header. The other two receivers on
that header (A4 and B4) are not used; they are there to locate the HX711
amplifier.

## Install the potentiometer

A potentiometer has three pins: 1 (fixed), 2 (wiper) and 3 (fixed). Here pin 1
is ground, pin 2 the output and pin 3 Vcc.

- Pin 1 (GND): F7
- Pin 2 (wiper): B8
- Pin 3 (Vcc): F9

## Install the jumper wires

This uses all the 22 AWG solid-core wires except the three 30 mm green ones.
The jumpers connect pins that are already installed to other installed pins:
each is run to a pad next to the pin of interest, and its extra lead is bent
over to touch the solder on that pin so the two can be soldered together. In
the table, each end is written `pad to insert into: pad to solder to`.

| Wire | End 1 | End 2 |
| --- | --- | --- |
| Green 40 mm | E13: E14 | M3: N3 |
| Yellow 40 mm | D13: D14 | M4: N4 |
| Yellow 40 mm | C13: C14 | M5: N5 |
| Red 45 mm | B13: B14 | M6: N6 |
| Green 20 mm | L3: M3 | G7: F7 |
| Red 25 mm | M14: N14 | G9: F9 |
| 220 Ω resistor | L14: M14 | I14 |

## Wire the button

Connect one of the green / green-white twisted pairs to the pins of the button,
covering the exposed wire with the two pieces of 1 mm heat shrink. The other
ends are attached to the breadboard last, because the button has to be
installed in place in the scale's housing.

## Wire the LCD

The LCD has 16 pins, numbered 1 (VSS) to 16 (LED−), as in the schematic. It is
wired with all the remaining twisted pairs and the three 30 mm pieces of green
solid-core wire.

1. Take the green / green-white pair. Connect one end of all three solid-core
   wires to one end of the green wire, making a three-wire pigtail, and cover
   the joint with the 3 mm heat shrink. This grounds the LCD.
2. Connect the three pigtail ends to pins 1, 5 and 16 of the LCD, and the
   matching end of the green-white wire to pin 15. The other end of this pair
   will go to the board to power the backlight.
3. Brown / brown-white pair: brown to 14, brown-white to 13.
4. Blue / blue-white pair: blue to 12, blue-white to 11.
5. Orange / orange-white pair: orange to 6, orange-white to 4.
6. Blue / orange pair: blue to 3, orange to 2.
7. Green / green-white pair: green to K3: L3, green-white to H14: I14.

Without shrinking it, slip the 5 mm heat shrink over the four single-colour
twisted pairs (leave the blue / orange pair free). **Do not shrink it yet.** It
will hold the wires together and out of the way of the load cell once the board
is complete.

Now attach the LCD to the breadboard, keeping in mind how the wires will lie in
the housing (dry-fit before cutting to length). The notation is the same as for
the jumpers: insert into the first pad, solder to the second. Soldering the pad
the wire is inserted into as well gives extra strength.

1. Blue / orange pair: blue to A8: B8, orange to F10: F9.
2. Brown / brown-white pair: brown to S6: T6, brown-white to S7: T7.
3. Blue / blue-white pair: blue to S8: T8, blue-white to S9: T9.
4. Orange / orange-white pair: orange to S10: T10, orange-white to S11: T11.

With the wires in place and lying properly in the housing, heat the heat shrink
to fix their shape and keep them off the load cell.

## Finish installing the button

This is the most awkward step, which is why this twisted pair has extra length.

1. Feed the green / green-white pair from the button through the hole in the
   face of the housing.
2. Connect green to J3: K3 and green-white to M10: N10.

## Install the board and LCD

If not already done, seat the LCD in its slot in the housing, routing its wires
around the load-cell boss. If any wire rests against the load cell, reliable
measurements are impossible. Seat the breadboard so that the Nano's USB port
will be reachable through the slot in the base; if it is not held tightly, hot
glue on two or three corners secures it.

## Finishing up

Put the Arduino Nano onto the two 15 × 1 headers and load a sketch that drives
only the LCD and prints something on it. (With the scale firmware, comment out
the initialisation of the balance, load cell and HX711 for this step, since the
HX711 is not installed yet and the firmware would wait for it.) The LCD is now
powered, but probably shows nothing legible: turn the potentiometer with a
screwdriver until the text is clearly visible. This sets the contrast and does
not need adjusting again.

Power down, plug the HX711 into the other female header, and install a load
cell, connecting it to the four male header pins.

The scale should now work. For the mechanical assembly and the load-cell
mounting, see Section 2.3 of the paper in [`paper/`](paper/), and for using the
scale, [`operation.md`](operation.md).

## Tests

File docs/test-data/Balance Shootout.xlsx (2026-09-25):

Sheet: 200623 - 100g Standard Mass
Mass Balance Test
Device Under Test: | OS_Nano_Balance (3D printed balance), Using TAL221 100g load cell
Lab Balance: | N/A Using standard masses
DUT Calibration: | Calibrated with 100 g standard mass
 | 13914.92 | g/div
 |  |  |  |  |  |  |  | PuTTY
 |  |  |  |  |  |  |  | -0.00462 | g
 |  |  |  |  |  |  |  | -0.00362 | g
 |  |  | Nominal | Average | Std | Count | Addresses | -0.00139 | g
 |  |  | 1.000 | 1.000213214 | 0.0025389383 | 28 | R22:R49 | -0.00169 | g
 |  |  | 2.000 | 1.994142069 | 0.0021695961 | 29 | R64:R92 | 0.00165 | g
 |  |  | 5.00 | 4.986438 | 0.0017971170 | 30 | R102:R131 | 0.00067 | g
 |  |  | 10.00 | 9.990840625 | 0.0017281763 | 32 | R140:R171 | 0.00118 | g
 |  |  | 20.00 | 19.99703759 | 0.0026241027 | 29 | R182:R210 | -6e-05 | g
 |  |  | 50.00 | 50.04050516 | 0.0056584860 | 31 | R221:R251 | 0.00119 | g
 |  |  | 1.00 | 1.019383824 | 0.0016537338 | 34 | R320:R353 | 0.00249 | g
 |  |  | 2.00 | 2.014557407 | 0.0012196557 | 27 | R369:R395 | 0.94735 | g
 |  |  | 5.00 | 5.006452414 | 0.0012887301 | 29 | R405:R433 | 1.00251 | g
 |  |  | 10.00 | 10.00825722 | 0.0019212722 | 36 | R444:R479 | 1.00552 | g
 |  |  | 20.00 | 20.01962429 | 0.0030291755 | 35 | R490:R524 | 1.002 | g
 |  |  | 50.00 | 50.05556625 | 0.0059257973 | 32 | R534:R565 | 1.0039 | g
 |  |  |  |  |  |  |  | 1.00243 | g
 |  |  |  |  |  |  |  | 1.00195 | g
 |  |  |  |  |  |  |  | 1.00197 | g
 |  |  |  | Avg | 0.0026295651 |  | 0.00263% | 0.99801 | g
 |  |  |  | Max | 0.0059257973 |  |  | 0.99988 | g
 |  |  |  |  |  |  |  | 0.99769 | g
 |  |  | 100.00 | 100.0766512 | 0.0109933918 | 34 | R267:R300 | 0.99878 | g
 |  |  | 100.00 | 100.0869182 | 0.0117700370 | 28 | R590:R617 | 0.99613 | g
 |  |  |  |  |  |  |  | 0.99817 | g
 |  |  |  |  |  |  |  | 1.00188 | g
 |  |  |  |  |  |  |  | 1.00118 | g
 |  |  |  |  |  |  |  | 1.003 | g
 |  |  |  |  |  |  |  | 1.00356 | g
 |  |  |  |  |  |  |  | 1.00209 | g
 |  |  |  |  |  |  |  | 1.00131 | g
 |  |  |  |  |  |  |  | 0.99666 | g
 |  |  |  |  |  |  |  | 0.99554 | g
 |  |  |  |  |  |  |  | 0.99851 | g
 |  |  |  |  |  |  |  | 0.99661 | g
 |  |  |  |  |  |  |  | 1.00077 | g
 |  |  |  |  |  |  |  | 0.99942 | g
 |  |  |  |  |  |  |  | 0.99858 | g
 |  |  |  |  |  |  |  | 0.99845 | g
 |  |  |  |  |  |  |  | 0.99947 | g
 |  |  |  |  |  |  |  | 1.13586 | g
 |  |  |  |  |  |  |  | 0.01222 | g
 |  |  |  |  |  |  |  | -0.00237 | g
 |  |  |  |  |  |  |  | -0.00142 | g
 |  |  |  |  |  |  |  | -0.00316 | g
 |  |  |  |  |  |  |  | -0.00131 | g
 |  |  |  |  |  |  |  | -0.00075 | g
 |  |  |  |  |  |  |  | -0.00137 | g
 |  |  |  |  |  |  |  | -0.00451 | g
 |  |  |  |  |  |  |  | -0.00584 | g
 |  |  |  |  |  |  |  | -0.00695 | g
 |  |  |  |  |  |  |  | -0.00574 | g
 |  |  |  |  |  |  |  | -0.00663 | g
 |  |  |  |  |  |  |  | 0.82138 | g
 |  |  |  |  |  |  |  | 1.992 | g
 |  |  |  |  |  |  |  | 1.98841 | g
 |  |  |  |  |  |  |  | 1.99106 | g
 |  |  |  |  |  |  |  | 1.99024 | g
 |  |  |  |  |  |  |  | 1.99114 | g
 |  |  |  |  |  |  |  | 1.99161 | g
 |  |  |  |  |  |  |  | 1.99457 | g
 |  |  |  |  |  |  |  | 1.99487 | g
 |  |  |  |  |  |  |  | 1.99423 | g
 |  |  |  |  |  |  |  | 1.99365 | g
 |  |  |  |  |  |  |  | 1.99517 | g
 |  |  |  |  |  |  |  | 1.99529 | g
 |  |  |  |  |  |  |  | 1.99538 | g
 |  |  |  |  |  |  |  | 1.99644 | g
 |  |  |  |  |  |  |  | 1.99497 | g
 |  |  |  |  |  |  |  | 1.99535 | g
 |  |  |  |  |  |  |  | 1.99557 | g
 |  |  |  |  |  |  |  | 1.99558 | g
 |  |  |  |  |  |  |  | 1.99497 | g
 |  |  |  |  |  |  |  | 1.99423 | g
 |  |  |  |  |  |  |  | 1.99339 | g
 |  |  |  |  |  |  |  | 1.99355 | g
 |  |  |  |  |  |  |  | 1.99352 | g
 |  |  |  |  |  |  |  | 1.99418 | g
 |  |  |  |  |  |  |  | 1.9957 | g
 |  |  |  |  |  |  |  | 1.99277 | g
 |  |  |  |  |  |  |  | 1.99606 | g
 |  |  |  |  |  |  |  | 1.99739 | g
 |  |  |  |  |  |  |  | 1.99883 | g
 |  |  |  |  |  |  |  | 1.59078 | g
 |  |  |  |  |  |  |  | -0.0078 | g
 |  |  |  |  |  |  |  | -0.00888 | g
 |  |  |  |  |  |  |  | -0.00739 | g
 |  |  |  |  |  |  |  | -0.00714 | g
 |  |  |  |  |  |  |  | -0.00618 | g
 |  |  |  |  |  |  |  | -0.00536 | g
 |  |  |  |  |  |  |  | 3.06891 | g
 |  |  |  |  |  |  |  | 4.98208 | g
 |  |  |  |  |  |  |  | 4.98418 | g
 |  |  |  |  |  |  |  | 4.98247 | g
 |  |  |  |  |  |  |  | 4.98471 | g
 |  |  |  |  |  |  |  | 4.9828 | g
 |  |  |  |  |  |  |  | 4.98413 | g
 |  |  |  |  |  |  |  | 4.98588 | g
 |  |  |  |  |  |  |  | 4.9863 | g
 |  |  |  |  |  |  |  | 4.98661 | g
 |  |  |  |  |  |  |  | 4.98576 | g
 |  |  |  |  |  |  |  | 4.98574 | g
 |  |  |  |  |  |  |  | 4.98498 | g
 |  |  |  |  |  |  |  | 4.98463 | g
 |  |  |  |  |  |  |  | 4.98714 | g
 |  |  |  |  |  |  |  | 4.98717 | g
 |  |  |  |  |  |  |  | 4.98665 | g
 |  |  |  |  |  |  |  | 4.98492 | g
 |  |  |  |  |  |  |  | 4.98975 | g
 |  |  |  |  |  |  |  | 4.98714 | g
 |  |  |  |  |  |  |  | 4.98814 | g
 |  |  |  |  |  |  |  | 4.98869 | g
 |  |  |  |  |  |  |  | 4.98817 | g
 |  |  |  |  |  |  |  | 4.98738 | g
 |  |  |  |  |  |  |  | 4.98517 | g
 |  |  |  |  |  |  |  | 4.98627 | g
 |  |  |  |  |  |  |  | 4.98676 | g
 |  |  |  |  |  |  |  | 4.98757 | g
 |  |  |  |  |  |  |  | 4.98785 | g
 |  |  |  |  |  |  |  | 4.98906 | g
 |  |  |  |  |  |  |  | 4.98824 | g
 |  |  |  |  |  |  |  | 4.98888 | g
 |  |  |  |  |  |  |  | 3.54671 | g
 |  |  |  |  |  |  |  | -0.00096 | g
 |  |  |  |  |  |  |  | -0.00776 | g
 |  |  |  |  |  |  |  | -0.0082 | g
 |  |  |  |  |  |  |  | -0.00803 | g
 |  |  |  |  |  |  |  | -0.00802 | g
 |  |  |  |  |  |  |  | 0.12763 | g
 |  |  |  |  |  |  |  | 9.98593 | g
 |  |  |  |  |  |  |  | 9.9867 | g
 |  |  |  |  |  |  |  | 9.98777 | g
 |  |  |  |  |  |  |  | 9.9882 | g
 |  |  |  |  |  |  |  | 9.98892 | g
 |  |  |  |  |  |  |  | 9.98982 | g
 |  |  |  |  |  |  |  | 9.98924 | g
 |  |  |  |  |  |  |  | 9.98969 | g
 |  |  |  |  |  |  |  | 9.98994 | g
 |  |  |  |  |  |  |  | 9.99 | g
 |  |  |  |  |  |  |  | 9.99 | g
 |  |  |  |  |  |  |  | 9.99068 | g
 |  |  |  |  |  |  |  | 9.98977 | g
 |  |  |  |  |  |  |  | 9.99189 | g
 |  |  |  |  |  |  |  | 9.99064 | g
 |  |  |  |  |  |  |  | 9.99043 | g
 |  |  |  |  |  |  |  | 9.991 | g
 |  |  |  |  |  |  |  | 9.99293 | g
 |  |  |  |  |  |  |  | 9.99221 | g
 |  |  |  |  |  |  |  | 9.99211 | g
 |  |  |  |  |  |  |  | 9.99209 | g
 |  |  |  |  |  |  |  | 9.99138 | g
 |  |  |  |  |  |  |  | 9.99172 | g
 |  |  |  |  |  |  |  | 9.99054 | g
 |  |  |  |  |  |  |  | 9.99003 | g
 |  |  |  |  |  |  |  | 9.99134 | g
 |  |  |  |  |  |  |  | 9.99238 | g
 |  |  |  |  |  |  |  | 9.99148 | g
 |  |  |  |  |  |  |  | 9.99232 | g
 |  |  |  |  |  |  |  | 9.98976 | g
 |  |  |  |  |  |  |  | 9.99414 | g
 |  |  |  |  |  |  |  | 9.993 | g
 |  |  |  |  |  |  |  | 9.99478 | g
 |  |  |  |  |  |  |  | 10.28653 | g
 |  |  |  |  |  |  |  | 0.36868 | g
 |  |  |  |  |  |  |  | -0.00103 | g
 |  |  |  |  |  |  |  | -0.00086 | g
 |  |  |  |  |  |  |  | -0.00185 | g
 |  |  |  |  |  |  |  | -0.00421 | g
 |  |  |  |  |  |  |  | -0.00407 | g
 |  |  |  |  |  |  |  | -0.00232 | g
 |  |  |  |  |  |  |  | -0.00382 | g
 |  |  |  |  |  |  |  | 13.60175 | g
 |  |  |  |  |  |  |  | 19.99067 | g
 |  |  |  |  |  |  |  | 19.99046 | g
 |  |  |  |  |  |  |  | 19.99238 | g
 |  |  |  |  |  |  |  | 19.99266 | g
 |  |  |  |  |  |  |  | 19.99561 | g
 |  |  |  |  |  |  |  | 19.99577 | g
 |  |  |  |  |  |  |  | 19.99607 | g
 |  |  |  |  |  |  |  | 19.99733 | g
 |  |  |  |  |  |  |  | 19.9953 | g
 |  |  |  |  |  |  |  | 19.99685 | g
 |  |  |  |  |  |  |  | 19.9982 | g
 |  |  |  |  |  |  |  | 19.99715 | g
 |  |  |  |  |  |  |  | 19.99667 | g
 |  |  |  |  |  |  |  | 19.99989 | g
 |  |  |  |  |  |  |  | 19.9992 | g
 |  |  |  |  |  |  |  | 20.00014 | g
 |  |  |  |  |  |  |  | 19.99877 | g
 |  |  |  |  |  |  |  | 20.00087 | g
 |  |  |  |  |  |  |  | 19.99641 | g
 |  |  |  |  |  |  |  | 19.99782 | g
 |  |  |  |  |  |  |  | 19.99874 | g
 |  |  |  |  |  |  |  | 19.99721 | g
 |  |  |  |  |  |  |  | 19.99875 | g
 |  |  |  |  |  |  |  | 19.99825 | g
 |  |  |  |  |  |  |  | 19.99783 | g
 |  |  |  |  |  |  |  | 19.99788 | g
 |  |  |  |  |  |  |  | 19.99808 | g
 |  |  |  |  |  |  |  | 19.99853 | g
 |  |  |  |  |  |  |  | 20.0006 | g
 |  |  |  |  |  |  |  | 20.08724 | g
 |  |  |  |  |  |  |  | 4.44233 | g
 |  |  |  |  |  |  |  | -0.00126 | g
 |  |  |  |  |  |  |  | -0.0002 | g
 |  |  |  |  |  |  |  | -0.00019 | g
 |  |  |  |  |  |  |  | -0.00041 | g
 |  |  |  |  |  |  |  | -0.00113 | g
 |  |  |  |  |  |  |  | -0.00064 | g
 |  |  |  |  |  |  |  | 16.51194 | g
 |  |  |  |  |  |  |  | 49.91961 | g
 |  |  |  |  |  |  |  | 50.02561 | g
 |  |  |  |  |  |  |  | 50.02888 | g
 |  |  |  |  |  |  |  | 50.03028 | g
 |  |  |  |  |  |  |  | 50.03382 | g
 |  |  |  |  |  |  |  | 50.03573 | g
 |  |  |  |  |  |  |  | 50.03483 | g
 |  |  |  |  |  |  |  | 50.03652 | g
 |  |  |  |  |  |  |  | 50.03774 | g
 |  |  |  |  |  |  |  | 50.03811 | g
 |  |  |  |  |  |  |  | 50.03751 | g
 |  |  |  |  |  |  |  | 50.03835 | g
 |  |  |  |  |  |  |  | 50.04054 | g
 |  |  |  |  |  |  |  | 50.0385 | g
 |  |  |  |  |  |  |  | 50.04148 | g
 |  |  |  |  |  |  |  | 50.04201 | g
 |  |  |  |  |  |  |  | 50.04051 | g
 |  |  |  |  |  |  |  | 50.04166 | g
 |  |  |  |  |  |  |  | 50.041 | g
 |  |  |  |  |  |  |  | 50.04189 | g
 |  |  |  |  |  |  |  | 50.04281 | g
 |  |  |  |  |  |  |  | 50.04432 | g
 |  |  |  |  |  |  |  | 50.04448 | g
 |  |  |  |  |  |  |  | 50.04558 | g
 |  |  |  |  |  |  |  | 50.04684 | g
 |  |  |  |  |  |  |  | 50.04562 | g
 |  |  |  |  |  |  |  | 50.0452 | g
 |  |  |  |  |  |  |  | 50.04654 | g
 |  |  |  |  |  |  |  | 50.0457 | g
 |  |  |  |  |  |  |  | 50.04784 | g
 |  |  |  |  |  |  |  | 50.04689 | g
 |  |  |  |  |  |  |  | 50.04887 | g
 |  |  |  |  |  |  |  | 45.58154 | g
 |  |  |  |  |  |  |  | 0.03114 | g
 |  |  |  |  |  |  |  | 0.02226 | g
 |  |  |  |  |  |  |  | 0.02045 | g
 |  |  |  |  |  |  |  | 0.01667 | g
 |  |  |  |  |  |  |  | 0.01572 | g
 |  |  |  |  |  |  |  | 0.01591 | g
 |  |  |  |  |  |  |  | 0.01341 | g
 |  |  |  |  |  |  |  | 0.01236 | g
 |  |  |  |  |  |  |  | 0.01248 | g
 |  |  |  |  |  |  |  | 0.00974 | g
 |  |  |  |  |  |  |  | 0.00903 | g
 |  |  |  |  |  |  |  | 0.00994 | g
 |  |  |  |  |  |  |  | 5.18872 | g
 |  |  |  |  |  |  |  | 96.91457 | g
 |  |  |  |  |  |  |  | 100.04342 | g
 |  |  |  |  |  |  |  | 100.0518 | g
 |  |  |  |  |  |  |  | 100.05706 | g
 |  |  |  |  |  |  |  | 100.06065 | g
 |  |  |  |  |  |  |  | 100.06392 | g
 |  |  |  |  |  |  |  | 100.0676 | g
 |  |  |  |  |  |  |  | 100.06964 | g
 |  |  |  |  |  |  |  | 100.0694 | g
 |  |  |  |  |  |  |  | 100.07191 | g
 |  |  |  |  |  |  |  | 100.07243 | g
 |  |  |  |  |  |  |  | 100.07587 | g
 |  |  |  |  |  |  |  | 100.07494 | g
 |  |  |  |  |  |  |  | 100.07478 | g
 |  |  |  |  |  |  |  | 100.07725 | g
 |  |  |  |  |  |  |  | 100.0759 | g
 |  |  |  |  |  |  |  | 100.07766 | g
 |  |  |  |  |  |  |  | 100.07821 | g
 |  |  |  |  |  |  |  | 100.07914 | g
 |  |  |  |  |  |  |  | 100.07967 | g
 |  |  |  |  |  |  |  | 100.08057 | g
 |  |  |  |  |  |  |  | 100.08369 | g
 |  |  |  |  |  |  |  | 100.08181 | g
 |  |  |  |  |  |  |  | 100.08246 | g
 |  |  |  |  |  |  |  | 100.08408 | g
 |  |  |  |  |  |  |  | 100.08357 | g
 |  |  |  |  |  |  |  | 100.08556 | g
 |  |  |  |  |  |  |  | 100.08727 | g
 |  |  |  |  |  |  |  | 100.08549 | g
 |  |  |  |  |  |  |  | 100.08839 | g
 |  |  |  |  |  |  |  | 100.0863 | g
 |  |  |  |  |  |  |  | 100.08875 | g
 |  |  |  |  |  |  |  | 100.08782 | g
 |  |  |  |  |  |  |  | 100.0891 | g
 |  |  |  |  |  |  |  | 100.09003 | g
 |  |  |  |  |  |  |  | 101.76251 | g
 |  |  |  |  |  |  |  | 18.72106 | g
 |  |  |  |  |  |  |  | 0.05402 | g
 |  |  |  |  |  |  |  | 0.04546 | g
 |  |  |  |  |  |  |  | 0.0406 | g
 |  |  |  |  |  |  |  | 0.03839 | g
 |  |  |  |  |  |  |  | 0.0337 | g
 |  |  |  |  |  |  |  | 0.03291 | g
 |  |  |  |  |  |  |  | 0.03345 | g
 |  |  |  |  |  |  |  | 0.0288 | g
 |  |  |  |  |  |  |  | 0.02723 | g
 |  |  |  |  |  |  |  | 0.02864 | g
 |  |  |  |  |  |  |  | 0.02646 | g
 |  |  |  |  |  |  |  | 0.02573 | g
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

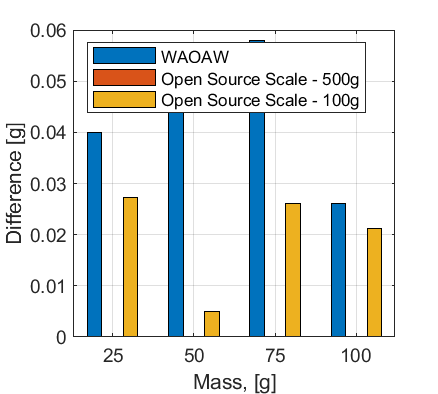
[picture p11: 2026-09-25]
docs/test-data/plots/100g Avg Diff.png

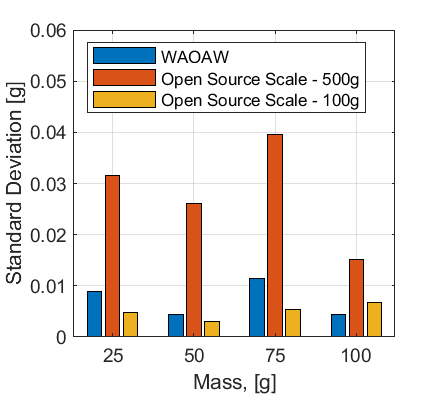
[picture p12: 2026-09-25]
docs/test-data/plots/100g Std.png

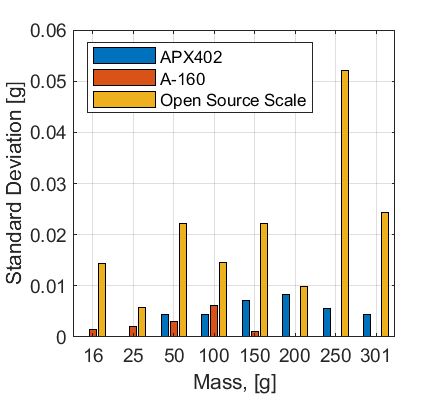
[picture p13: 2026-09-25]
docs/test-data/plots/500g Std.png

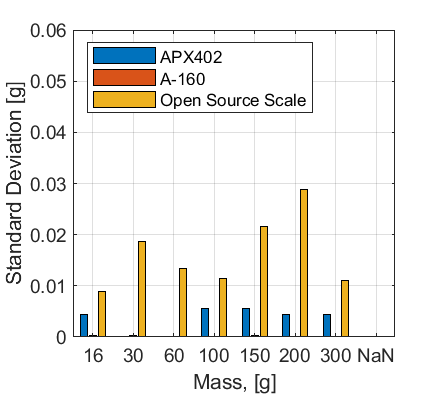
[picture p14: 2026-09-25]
docs/test-data/plots/5kg Std.png

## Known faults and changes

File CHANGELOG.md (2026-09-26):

# Changelog

All notable changes to this project are documented in this file.

The format loosely follows [Keep a Changelog](https://keepachangelog.com/en/1.1.0/)
and [Semantic Versioning](https://semver.org/spec/v2.0.0.html).

## [Unreleased]

### The three generations joined (2026-09)

The repository, now `mass-scale`, carries the full histories of
Benjamin Hubbard's 2019 [OS Nano Balance](https://github.com/brhubbar/OS_Nano_Balance)
(tag `mtu-nanobalance-2019`) and of the FAST research group's 2025–26 revival,
[uwo-fast/mass-scale](https://github.com/uwo-fast/mass-scale) (tag
`fast-revival-2026`), beside the 2020 history already here. Each was merged
unchanged under a staging folder and then sorted into place in commits that
only move files, so `git log --follow` reaches every file's origin. Nothing
was rewritten.

#### Added

- `cad/openscad/`: the revival's OpenSCAD v2 enclosure, platter and assembly,
  the current design; `cad/openscad-v3/`: the v3 revision in progress, with
  the four files of [load-cell-scad](https://github.com/CameronBrooks11/load-cell-scad)
  it includes vendored under `lib/` at commit `c8f224a` (`GPL-3.0`, with a
  provenance README) and its includes pointed there, so it renders from a
  plain clone; `cad/openscad-v1/`: the revival's reformatting of the 2019
  OpenSCAD parts.
- `cad/freecad-2019/`: Hubbard's three FreeCAD parts and `Parameters.csv`,
  with the OSF revision of the base kept beside his as `Base-osf.FCStd` and a
  README saying which is which; `cad/openscad-2019/`: his original OpenSCAD
  parts.
- `firmware/mass-scale/`: the revival's rewritten firmware, the current one,
  with its README made plain Markdown (it was wrapped in a code fence).
- `firmware/os-nano-balance-2019/`: Hubbard's 2019 sketch and project README.
- `docs/datasheets/1602LCD.pdf`, the 1602A LCD reference the 2019 project
  carried.
- `just check-scad` (and `cad/scad-parts.tsv`): renders the v2 and v3 parts
  with `--hardwarnings`, `OPENSCAD` naming the command and `OPENSCAD_FLAGS`
  adding flags; `just render` writes them to `build/cad/openscad/`.
- `just firmware-libs`: fetches bogde/HX711 0.7.5 and
  arduino-libraries/LiquidCrystal 1.0.7 as release tarballs, checks their
  SHA-256s, and `check-firmware` and `firmware` build `firmware/mass-scale`
  against them with `--library`, ahead of any library of the same name
  installed for the user.
- The CI workflow installs OpenSCAD and can be started by hand.
- A History section in the README, a `cad/freecad-2019/README.md`, a new
  `firmware/README.md` covering all three generations with the shared wiring,
  and `CITATION.cff` references for the 2019 and revival work.

#### Changed

- The 2020 design moved to `cad/freecad-2020/` (document and `stl/`), the
  2020 firmware to `firmware/most-massbalance-2020/`; `cad/parts.tsv` and the
  guides that name them follow. These commits only move files.
- `LICENSING.md` covers the 2019 files, the revival's firmware and designs and
  the vendored library, and reads Hubbard's bare GPL-3.0 licence file as
  or-later under the standing practice already applied to the 2020 files.
- Every self reference is `mass-scale`.

#### Removed

- The Scale Manufacturers Association's SCP-0499 standard and Load Cell
  Application and Test Guideline from `docs/datasheets/`: the association's
  publications, linked from the datasheets README instead (its site and the
  Wayback Machine). Both remain in the history.
- Duplicates, byte for byte the files kept: the revival's copies of the 2019
  FreeCAD parts and of the 2020 document, the 2019 and revival copies of the
  datasheets, and the OSF copies of the 2019 `Bed.FCStd` and `Face.FCStd`.
- Files the merged tree supersedes: the 2019 and revival `LICENSE`,
  `.gitignore` and `.gitattributes`, the revival's project README (its
  wiring and serial notes moved into `firmware/README.md`), the 2019 sketch's
  HX711 submodule, and two scratch files of the v2 `lib/` (one empty, one
  written against a load-cell-scad API that no longer exists).

### Imported from MOST (2026-09)

Imported into uwo-fast from
[mtu-most/most_massbalance](https://gitlab.com/mtu-most/most_massbalance), with
its full history (the firmware the paper describes is tagged
`mtu-instruments-2020`, upstream's last commit `mtu-final-2021`, and upstream's
own `v3.0.0` to `v3.4.0` tags are kept), and the design files from
[OSF me9a8](https://osf.io/me9a8), imported unchanged in the commit tagged
`mtu-osf-2020`. Paths below are as they were at the time; the CAD is now under
`cad/freecad-2020/` and the firmware under `firmware/most-massbalance-2020/`.

#### Added

- `cad/`: the FreeCAD assembly with its four bodies, the three earlier part
  files, and the four published STLs, from OSF.
- `firmware/DigitalMassBalance/`: the 2.0.1 sketch the paper describes, with
  the HX711 and LiquidCrystal libraries it bundles, from OSF.
- `firmware/MOST_MassBalance/src/HX711/`: the HX711 library at the commit the
  submodule pinned (0.7.4, `MIT`), in place of the submodule.
- `electronics/`: the Fritzing renderings from OSF beside the Fritzing sketch
  from upstream.
- `docs/`: the component datasheets and the SMA protocol, the test logs,
  spreadsheet and plots, the paper (`CC-BY-4.0`), an operation guide adapted
  from it, the breadboard assembly guide adapted from Appropedia with its
  photographs, and a sources page; READMEs for `cad/`, `firmware/`,
  `electronics/` and `bom/`, with the paper's bill of materials as tables.
- `justfile` with `check` (verify every FreeCAD document and published STL,
  build both firmware targets), `firmware-deps`, `firmware` and `stl-stats`,
  and a CI workflow running `just check`.
- `cad/parts.tsv`, the list of bodies and their published STLs, and
  `tools/stlcmp.py`, which reports an STL's volume and bounding box.
- `tools/export_freecad.py` and `just compare-freecad`, which re-export every
  body from `Mass Balance.FCStd` under `freecadcmd` and compare the exports
  with the published STLs. Top, Bed and Cover match; the published `Base.stl`
  is 1.25 % smaller than the document's base and predates its last save
  (`cad/README.md`).
- `README.md`, `LICENSING.md` with the licence texts, `CITATION.cff`, and the
  FAST template's editor and line-ending configuration.

#### Changed

- The library moved to `firmware/MOST_MassBalance/`, its Fritzing circuit to
  `electronics/` and its protocol notes to `docs/serial-protocol/`; the OSF
  files sorted into `cad/`, `firmware/`, `electronics/` and `docs/`. These
  commits only move files.
- The STL archive is stored as its four files.
- Line endings normalized to LF.

#### Fixed

- Both sketches included their headers with backslashes, so they compiled only
  on Windows. With forward slashes they build everywhere.
- The 2020 sketch included its bundled libraries at the paths its git
  submodules had (`HX711/src/HX711.h`), which the OSF upload does not have.
  The includes now point at the files as published.

With those changes, the 2020 sketch and the library's example both build for an
Arduino Nano with arduino-cli.

#### Removed

- The OSF copies of the Fritzing circuit and the two protocol notes, which
  duplicate the upstream files byte for byte, and the sketch's stale
  `.gitmodules` and `.gitignore`.
- The operator manuals of the two Denver Instruments balances the paper
  compared against, and the Scale Manufacturers Association's protocol tester
  program: third-party material that is not part of the design.
- The 370 MB use video was never committed; it is attached to the first
  release instead.

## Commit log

2020-01-08 Adds circuit diagram from Fritzing; ignores .png outputs from Fritzing file.
    [Circuit Diagram.fzz]
2020-04-07 Clears out unnecessary returns and print statements for readibility and conciceness.
2020-04-08 Removes printToSerialAndDisplay to make room for properly formatted responses without harming printToDisplay
2020-04-08 Implements silent tare(), zero(), and clearTare() (no serial output) and corrects bug from using println instead of print.
2020-04-09 Separate report rate from sample rate.
2020-04-09 Serially command calibration sequence using <LF>Xc<CR> or <LF>Xc<xxxxxx.xxx><CR> Buggy; needs unit receptivity.
2020-04-09 Adds response for calibration sequence and allows escape from calibration.
2020-04-09 Cleans up circuit diagram.
    [Circuit Diagram.fzz]
2020-04-15 Adds command to toggle power to the LCD.
2020-06-28 Implement index for averaging filter to improve efficiency for long averages
    Replaces shifting the entire array which involved a lot of memory reassignment.
2020-06-28 Move clearTareSilent into calibrate() for DRYness
2020-06-28 Remove low-pass filter TODO
    This was initially intended to act as a noise filter but has been determined unnecessary.
    <https://stanford.edu/~boyd/ee102/conv_demo.pdf>
2020-06-29 Revert "Implement index for averaging filter to improve efficiency for long averages"
    This reverts commit 9fdd90d45a6d878a5718575427b7eb87edd4a671.
2020-07-01 Remove debugging print statements
2020-07-07 Note in README that only certain boards can run OLED thanks to memory limitations
2020-08-04 Make report rate independent of processing delays
    report rate was previously affected by the time taken to save to
    'lastRefresh', making the report rate slower than specified.
    Now, report rate compares the current time to the last refresh using
    an integer count of the number of cycles since the last refresh.
2021-02-23 Call millis() once per iteration to improve report_rate behavior
2025-03-05 updated cad to new version
    [Base.FCStd, Base.scad, Bed.FCStd, Bed.scad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]
2025-03-07 updates to new openscad
    [assembly.scad, enclosure.scad, load_cell_lib_usage.scad, platter.scad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]
2025-10-12 finalize mvp of casing for scad v2
    [_settings.scad, assembly.scad, enclosure.scad, load_cell_lib_usage.scad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]
2025-10-12 print v0 of openscadv2 enclo and platter
    [assembly.scad, enclosure.scad]
2025-10-12 thicken walls for 0.8n printer
    [assembly.scad]
2025-10-12 minor format
    [assembly.scad]
2026-06-26 fix(firmware): restore working calibration in mass-scale
    The serial rewrite never actually applied its stored calibration and
    computed a wrong sensitivity when calibrating, so it could not work in
    the field. Fix the calibration path end to end:
    - stop overwriting the EEPROM-loaded value with default_scale on load
    - calibrate from the raw, tare-subtracted reading (get_value) instead of
    get_units, which divided by the previous scale
    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
2026-06-26 fix(firmware): restore raw+calibrated readout and stop LCD flicker
    The rewrite left the non-blocking timing scaffolding unused, cleared the
    LCD every loop (flicker), printed only the calibrated value mislabeled as
    "Raw value", and chose decimal places by counting digits of a noisy float
    (jittery, meaningless).
    - gate measurement/display behind the previousMillis/interval timer while
    polling serial and the tare button every iteration
    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
2026-06-26 docs(readme): document serial-driven firmware and update wiring
    The README still described the original button-driven workflow after the
    cutover to the serial-driven mass-scale sketch.
    - retitle from OS_Nano_Balance and reword the provenance line
    - drop the D7 calibration button from the wiring; calibration is serial
    - rewrite the Tare/Calibrate sections for the t / c / u00 / aXY commands
    - note the bogde/HX711 library dependency
2026-06-29 initial commit of v3
    [_settings.scad, assembly.scad, enclosure.scad, platter.scad]
2026-06-29 first pass of v3 scad
    [_settings.scad, assembly.scad, enclosure.scad, mass-scale.scad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]
2026-06-29 center scale v3 scad
    [mass-scale.scad]
2026-06-29 first pass print of v3 scad
    [mass-scale.scad]
2026-06-30 revise guides so theres an opening mouth and latching post
    [mass-scale.scad]
